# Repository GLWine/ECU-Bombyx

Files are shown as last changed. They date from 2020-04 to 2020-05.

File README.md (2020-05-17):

# ECU documentation for Bombyx mori





Thesis project on the effects of climate and gases in companies that produce silk. Use of an Arduino system called ECU-Bombyx (Environmental control unit - Bombyx Mori).

Purpose: to measure changes in temperature, humidity, eCO2 and total volatile organic compounds (TVOC) to correlate any effects on the yarn obtained.
The project consists of an Arduino, a humidity and temperature sensor, a clock module, an SD card shield and an SGP30 sensor for air quality.
Every 15 minutes The ECU-BM performs a reading that it saves in the SD.

<table cellspacing=”0″ cellpadding=”0″ width=”560″ border="0">
<tbody>
<tr>
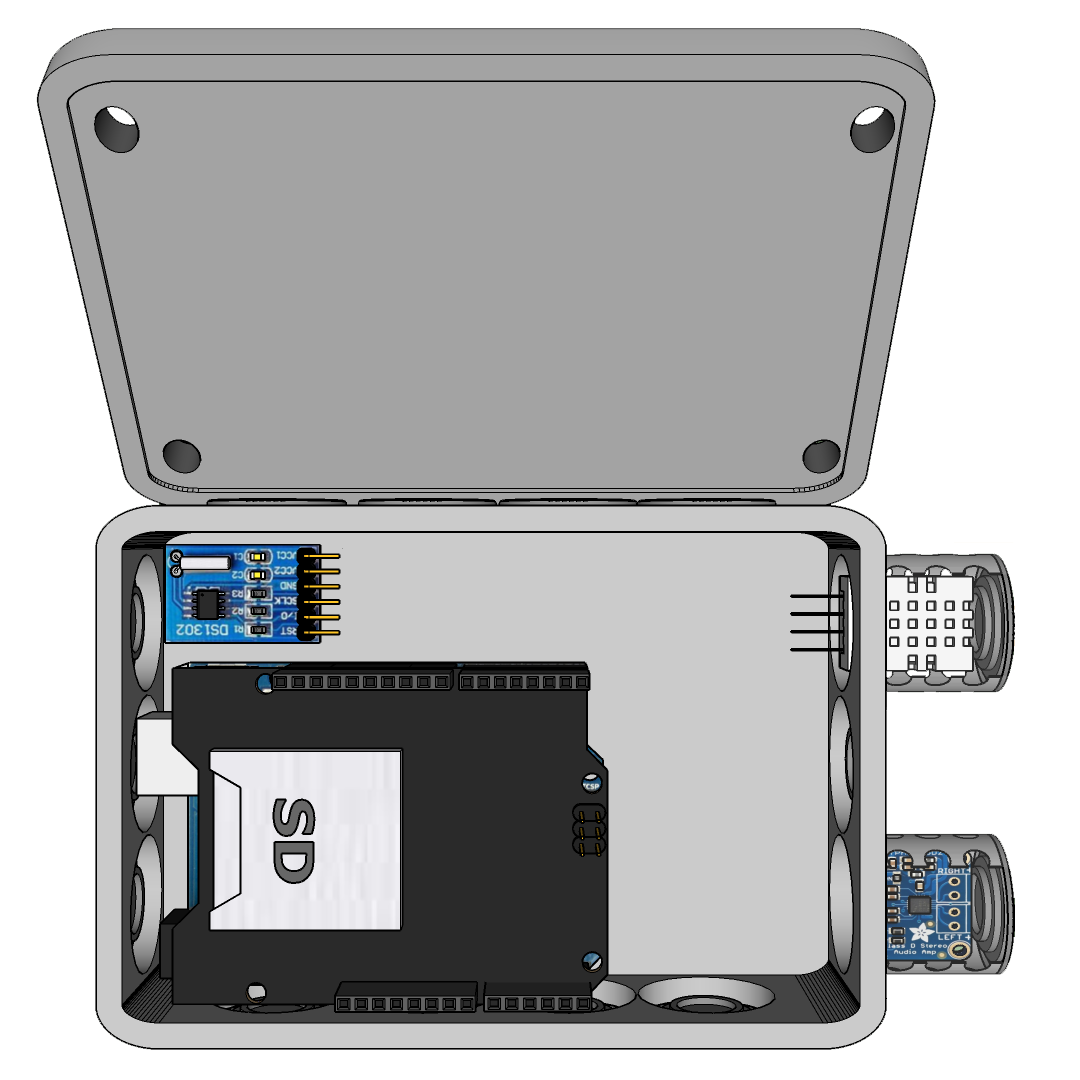
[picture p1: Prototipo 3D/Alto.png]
<td valign=”top” width=”250”></td>
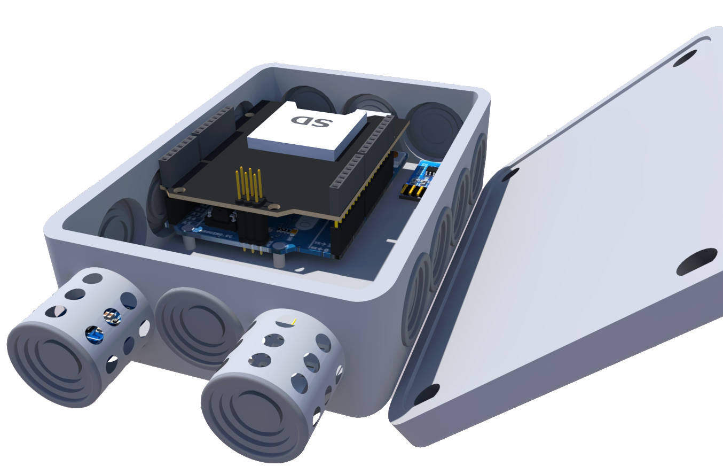
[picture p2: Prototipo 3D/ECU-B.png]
<td valign=”top” width=”250”></td>
</tr></tbody></table>

# Installation guide

## Phase 1: *wiring*
Before installing and starting make sure of the presence of these modules:
- DHT 22 sensor (temperature and humidity);
- Micro-SD module;
- RTC DS1302 module (clock);
- SGP30 air quality sensor;
- Arduino module one turn. 3;
Strictly carry out the wiring as indicated in the ECU-Bombyx image.

## Phase 2: *software installation*
Step 0: install the necessary libraries.

Step 1: install the ECU-Bombyx-Setter file from the Arduino IDE. In the "Serial monitor" view, make sure all modules respond.

--- Skip if the previous one is successful ---

Step 2: carefully check the wiring and that the modules are actually working.

Step 3: install the ECU-Bombyx-Base-Line file from the Arduino IDE. This is to find the baseline for the SGP30 sensor. Based on the [manufacturer's information](https://github.com/adafruit/DHT-sensor-library/pull/138 "Baseline Set & Get"), I created the code. This passage is of fundamental importance. The procedure lasts 12, it must be done for each SGP30 you have.

Step 4: install the ECU-Bombyx-Main file from the Arduino IDE. In the "Serial monitor" view, make sure that all modules respond and complete operations.

Final notes:
1. will start reading every 15 minutes writing in the micro-SD. The save format is .cvs with the company name.
2. If the DHT 22 module does not mount a 4K7 Ohm resistor, it is essential to solder one between DAT and VDD.
3. (optional) Add a 100nF capacitor between VDD and GND for filtering the waves.
3. There is a voluntary error in the ECU-BOMBYX-Main code. The reason is to remind those who use the code to set the variable that gives the name the file with the readings.

# Libraries

I made some changes to it based on this libbrerie of DHT [Pull requests #138](https://github.com/adafruit/DHT-sensor-library/pull/138 "Fixed signed/unsigned and unused parameter warnings")

The library to be imported with the correction is in the zip, it is sufficient to decompress it in the folder ..\Documents\Arduino\libraries\.

## Libraries List

Here are the lepers used for the code:

- Adafruit SGP30 Air Quality Sensor Breakout
  - Adafruit SGP30 Sensor by Adafruit V.1.2.0
- DS1302: Trickle-Charge Timekeeping Chip
  - RTC by Makuna V.2.3.4
- DHT22 temperature-humidity sensor + extras
  - DHT sensor librery by Adafruit V.1.3.9 **_modified_**

I recommend installing all the dependencies that arduino IDE offers

# License   

This program is free software: you can redistribute it and/or modify
it under the terms of the GNU General Public License as published by
the Free Software Foundation, either version 3 of the License, or
(at your option) any later version.

This program is distributed in the hope that it will be useful,
but WITHOUT ANY WARRANTY; without even the implied warranty of
MERCHANTABILITY or FITNESS FOR A PARTICULAR PURPOSE.  See the
GNU General Public License for more details.

You should have received a copy of the GNU General Public License
along with this program.  If not, see <http://www.gnu.org/licenses/>.

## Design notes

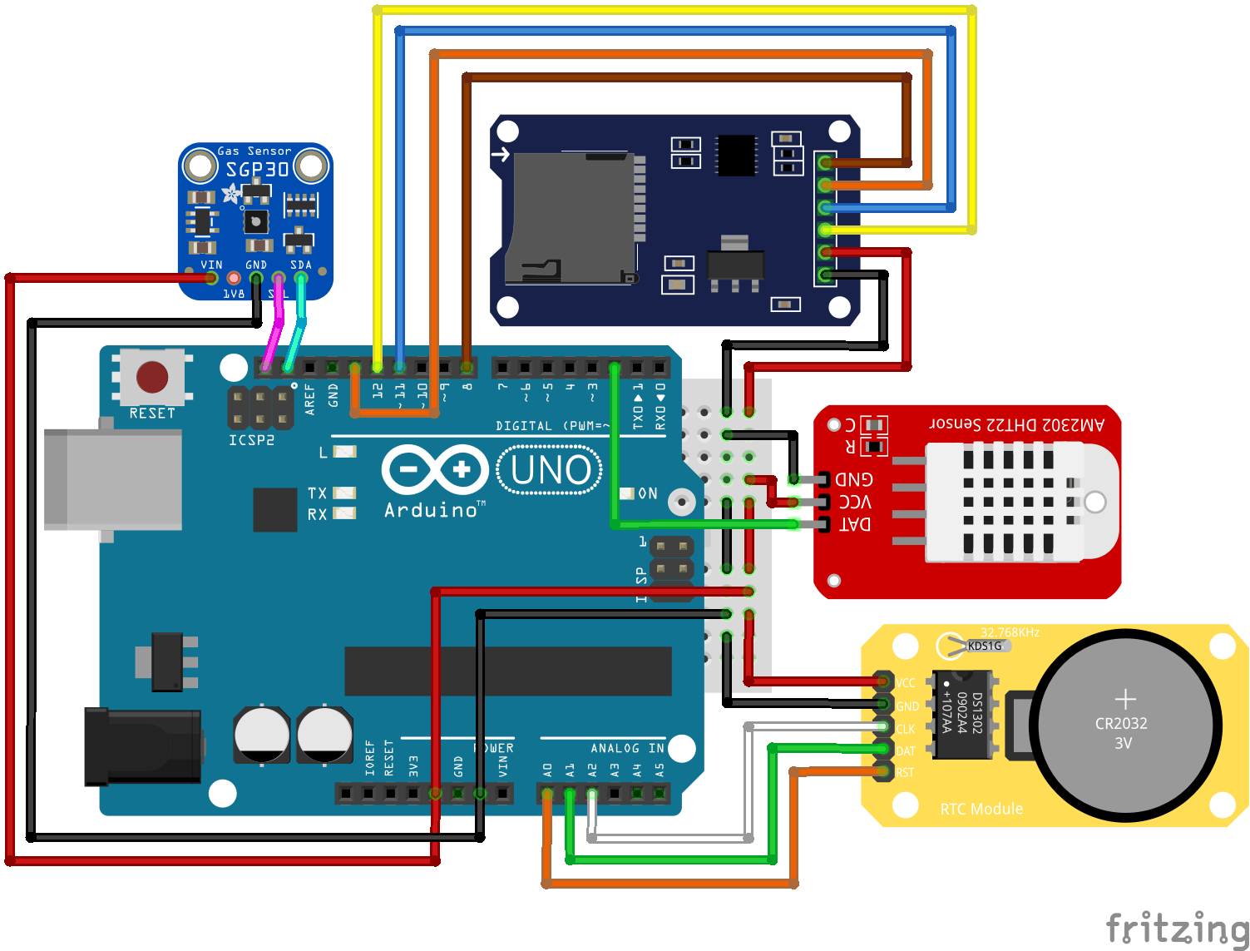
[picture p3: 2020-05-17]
ECU design on Fritzing/ECU-Bombyx.png

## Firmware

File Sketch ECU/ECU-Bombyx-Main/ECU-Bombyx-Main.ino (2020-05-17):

/* The following code is used to set the various components and to verify that 
 * everyone answers the call. It is written on the right serial monitor. 
 * The data are conveyed into a single variable then written into the SD.
 * 
 * modified 17 May 2020 by Giampiero Leserri
 */

// ADD the following Arduino libraries:
#include <SPI.h>            // standard Arduino library
#include <SD.h>             // standard Arduino library
#include <Wire.h>           // standard Arduino library
#include <Adafruit_SGP30.h> //Adafruit SGP30 Sensor by Adafruit V1.2.0
#include <ThreeWire.h>      // RTC: RTC by Makuna V.2.3.4
#include <RtcDS1302.h>      // RTC: RTC by Makuna V.2.3.4
#include <DHT.h>            /* DHT: DHT sensor librery by Adafruit V.1.3.9
                            *       Adafruit Unified Sensor by Adafruit V.1.1.2                        
                            *       Adafruit ADXL343 by Adafruit V.1.2.0 
                            */

// set up variables using the DHT 22:
#define DHTPIN 2          //Pin select DHT
#define DHTTYPE DHT22     // DHT 22  (AM2302), AM2321
DHT dht(DHTPIN, DHTTYPE); // Declare the DHT data pin and model to the DHT library

// set up variables using the SD utility library functions:
#define chipSelect 4 // declare the pin that is connected to the chip select
File myFile;         // the myFile object is created for the SD

// set up variables using the DS1302 RTC:
ThreeWire myWire(15, 16, 14); // DAT->pin A1, CLK->pin A2, RS->pin A0
RtcDS1302<ThreeWire> Rtc(myWire);
#define countof(a) (sizeof(a) / sizeof(a[0]))

// set up variables using the sgp30:
Adafruit_SGP30 sgp;
uint16_t TVOC_base, eCO2_base;
float temperature = 0; // [°C]
float humidity = 0;    // [%RH]
uint32_t getAbsoluteHumidity(float temperature, float humidity)
{
  // approximation formula from Sensirion SGP30 Driver Integration chapter 3.15
  const float absoluteHumidity = 216.7f * ((humidity / 100.0f) * 6.112f * exp((17.62f * temperature) / (243.12f + temperature)) / (273.15f + temperature)); // [g/m^3]
  const uint32_t absoluteHumidityScaled = static_cast<uint32_t>(1000.0f * absoluteHumidity);                                                                // [mg/m^3]
  return absoluteHumidityScaled;
}

// declaration of the Global variables make a string
//  for assembling the data to log
String dataOnTtheRow = "";

// Enter the initial company name without spaces followed by a progressive number
// for each ECU installed, also entering ".csv" (maximum 6.3 characters)
// Ex. Seta Etica ECU 1 => "SeEt01.csv"
const String company = "xxxxxx.csv"!;  // this error allows you not to forget to set the company name

// variable to which the 15 minutes to take the readings are added
uint32_t pouse = 0;
// Variable content in the if on line xxx,
// this causes every 4 readings to set the new baseline
int8_t c = 0;

//*********************************************************************************
void setup()
{
  // Open serial communications and wait for port to open:
  Serial.begin(9600); // 9600 bps serial port setting
  delay(500);

  rtcSet();
  sdSet();
  DHTSet();
  sgp30Set();
}

void loop()
{
  // If 15 minutes of use have passed a reading
  if (millis() > pouse)
  {
    // Further increase of 15 the pauseMain value, causes overflow
    pouse += (15UL * 60UL * 1000UL);
    heatingSgp30();

    delay(2000); // Safety delay in case of DHT reset
    rtcMain();
    DHTMain();
    sgp30Main();
    sdMain();
    c += 1;
  }
}
//---------------------------------------------------------------------------------

// Group of functions for setting the modules
//*********************************************************************************

// The function takes care of starting and if necessary
// setting the date and time of the DS1302
void rtcSet()
{
  Rtc.Begin();
  Serial.println(F("RTC initialized!"));

  if (Rtc.GetIsWriteProtected())
  {
    //      Serial.println(F("RTC was write protected, enabling writing now"));
    Rtc.SetIsWriteProtected(false);
  }

  if (!Rtc.GetIsRunning())
  {
    //      Serial.println(F("RTC was not actively running, starting now"));
    Rtc.SetIsRunning(true);
  }
}

// The function takes care of starting the SD module and, if necessary,
// creating a "CSV" file with the current date
void sdSet()
{
  Serial.print(F("Initializing SD card..."));

  // See if the card is present and can be initialized:
  if (!SD.begin(chipSelect))
  {
    Serial.println(F("Card failed, or not present"));
  }
  Serial.println(F("card initialized."));

  // Check if there is a file with the name given by the variable "company",
  // otherwise it creates and initializes it
  if (!SD.exists(company))
  {
    myFile = SD.open(company, FILE_WRITE);
    myFile.println(F("Data & Time;C-Temp;%-Humid;ppm-eCO2;ppb-TVOC;"));
    myFile.close();
    Serial.print(company);
    Serial.println(F(" file created"));
  }
}

// initialazied DHT22
void DHTSet()
{
  dht.begin();
  Serial.println(F("DHT22 initialized!"));
}

void sgp30Set()
{
  if (!sgp.begin())
  {
    Serial.println(F("Sensor not found :("));
  }
  else
  {
    Serial.println(F("SGP30 initialized!"));
  }
  Serial.print(F("Found SGP30 serial #"));
  Serial.print(sgp.serialnumber[0], HEX);
  Serial.print(sgp.serialnumber[1], HEX);
  Serial.println(sgp.serialnumber[2], HEX);

  // open the ECO2.TXT for reading:
  myFile = SD.open("eCO2.txt");
  if (myFile)
  {
    Serial.println(F("\neCO2.txt read... "));

    // read from the file until there's nothing else in it:
    while (myFile.available())
    {
      dataOnTtheRow = myFile.readStringUntil('\n');
      dataOnTtheRow.replace("\n", "");
      // goes to convert the string hexadecimal into a integer
      eCO2_base = strtoul(dataOnTtheRow.c_str(), NULL, 16);
      Serial.println(F("Print eCO2_base"));
      Serial.println(eCO2_base, HEX);
    }
    // close the file:
    myFile.close();
  }
  else
  {
    // if the file didn't open, print an error:
    Serial.println(F("error opening ECO2.TXT"));
  }

  // open the TVOC.TXT for reading:
  myFile = SD.open("TVOC.txt");
  if (myFile)
  {
    Serial.println(F("TVOC.TXT read... "));

    // read from the file until there's nothing else in it:
    while (myFile.available())
    {
      dataOnTtheRow = myFile.readStringUntil('\n');
      dataOnTtheRow.replace("\n", "");
      // goes to convert the string hexadecimal into a integer
      TVOC_base = strtoul(dataOnTtheRow.c_str(), NULL, 16);
      Serial.println(TVOC_base, HEX);
    }

    // close the file:
    myFile.close();
  }
  else
  {
    // if the file didn't open, print an error:
    Serial.println(F("error opening TVOC.TXT"));
  }

  // it sets the baseline calculated in 12 hours
  if (!sgp.setIAQBaseline(eCO2_base, TVOC_base))
  {
    Serial.println(F("the baseline was not written!"));
  }
}
//---------------------------------------------------------------------------------

// Group of functions for utilized the modules
//*********************************************************************************

// The function takes care of heating the sgp30 module
void heatingSgp30()
{
  humidity = dht.readHumidity();
  temperature = dht.readTemperature();
  sgp.setHumidity(getAbsoluteHumidity(temperature, humidity));
  for (int i = 0; i <= 30; i++)
  {
    sgp.IAQmeasure();
    delay(1000);
  }
  // Notice of end of heating
  Serial.println(F("heating finished"));

  if (c == 4)
  {
    sgp.getIAQBaseline(&eCO2_base, &TVOC_base);
    sgp.setIAQBaseline(eCO2_base, TVOC_base);
    c = 0;
  }
}

// The function starts writing in the string that forms the first line
void rtcMain()
{
  // I create a DateTime object and call it now
  // and pass it the constructor rtc.now();
  RtcDateTime now = Rtc.GetDateTime();
  printDateTime(now);

  if (!now.IsValid())
  {
    Serial.println();
    // Common Causes:
    // the battery on the device is low or even missing and
    // the power line was disconnected
    Serial.println(F("RTC lost confidence in the DateTime!"));
  }
}

// The function converts and writes the time to the dataOnTtheRow variable
void printDateTime(const RtcDateTime &dt)
{
  char datestring[20];

  snprintf_P(datestring,
             countof(datestring),
             PSTR("%04u/%02u/%02u %02u:%02u"),
             dt.Year(),
             dt.Month(),
             dt.Day(),
             dt.Hour(),
             dt.Minute());
  dataOnTtheRow = String(datestring);
  dataOnTtheRow += (F(";"));
}

// Function for reading humidity and temperature
void DHTMain()
{
  // Reading temperature or humidity takes about 250 milliseconds!
  // Sensor readings may also be up to 2 seconds 'old' (its a very slow sensor)
  float h = dht.readHumidity();
  // Read temperature as Celsius (the default)
  float t = dht.readTemperature();

  // Writing of the values read in the two variables
  if (isnan(h) || isnan(t))
  {
    Serial.println(F("Failed to read from DHT sensor!"));
  }

  // Passing data to the variable that will write to the SD
  dataOnTtheRow += (t);
  dataOnTtheRow += (F(";"));
  dataOnTtheRow += (h);
  dataOnTtheRow += (F(";"));
}

void sgp30Main()
{
  c = c + 1;
  delay(2000);
  // If you have a temperature / humidity sensor, you can set the absolute
  // humidity to enable the humditiy compensation for the air quality signals
  humidity = dht.readHumidity();
  temperature = dht.readTemperature();
  sgp.setHumidity(getAbsoluteHumidity(temperature, humidity));
  if (!sgp.IAQmeasure())
  {
    dataOnTtheRow += (F("sgp not read; sgp not read;"));
  }
  else
  {
    dataOnTtheRow += (sgp.eCO2);
    dataOnTtheRow += (F(";"));
    dataOnTtheRow += (sgp.TVOC);
    dataOnTtheRow += (F(";"));
  }
}

// Function that writes the data collected in the SD
void sdMain()
{
  // open the file. note that only one file can be open at a time,
  // so you have to close this one before opening another.
  myFile = SD.open(company, FILE_WRITE);

  // if the file is available, write to it:
  if (myFile)
  {
    myFile.println(dataOnTtheRow);
    myFile.close();
    Serial.println(F("String:"));
    Serial.println(dataOnTtheRow);
    Serial.print(company);
    Serial.println(F(" update!\n"));
  }
}
//---------------------------------------------------------------------------------
//Sketch uses 25922 bytes (80%) of program storage space. Maximum is 32256 bytes.
//Global variables use 1164 bytes (56%) of dynamic memory,
//leaving 884 bytes for local variables. Maximum is 2048 bytes.

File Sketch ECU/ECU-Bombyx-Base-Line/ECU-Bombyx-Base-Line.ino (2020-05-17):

/* The following code is used to set the starting baseline for the SGP30 module.
 * The calibration process lasts 12 hours, every 30 minutes from a partial response.
 * At the end he writes in the SD the two found values of the eCO2 and of the TVOC.
 * 
 * modified 17 May 2020 by Giampiero Leserri
 */

#include <SPI.h>
#include <SD.h>
#include <Wire.h>
#include <Adafruit_SGP30.h>
#include <DHT.h>

// set up variables using the DHT 22:
#define DHTPIN 2          //Pin select DHT
#define DHTTYPE DHT22     // DHT 22  (AM2302), AM2321
DHT dht(DHTPIN, DHTTYPE); // Declare the DHT data pin and model to the DHT library

// set up variables using the SGP30:
Adafruit_SGP30 sgp;
uint16_t TVOC_base, eCO2_base;
/* return absolute humidity [mg/m^3] with approximation formula
* @param temperature [°C]
* @param humidity [%RH]
*/
uint32_t getAbsoluteHumidity(float temperature, float humidity)
{
  // approximation formula from Sensirion SGP30 Driver Integration chapter 3.15
  const float absoluteHumidity = 216.7f * ((humidity / 100.0f) * 6.112f * exp((17.62f * temperature) / (243.12f + temperature)) / (273.15f + temperature)); // [g/m^3]
  const uint32_t absoluteHumidityScaled = static_cast<uint32_t>(1000.0f * absoluteHumidity);                                                                // [mg/m^3]
  return absoluteHumidityScaled;
}

// set up variables using the SD utility library functions:
#define chipSelect 4 // declare the pin that is connected to the chip select
// the myFile object is created for the SD
File myFilex;
File myFiley;

//
const unsigned long timeL = 44100000;  //12 hour
static unsigned long timeS1 = 60000;   // 1 minute
static unsigned long timeS2 = 1800000; //30 minute

//const unsigned long timeL = 600000; //10 minute
//static unsigned long timeS1 = 60000; // 1 minute
//static unsigned long timeS2 = 300000; //5 minute

void setup()
{
  Serial.begin(9600);

  Serial.print(F("Initializing SD card..."));

  if (!SD.begin(4))
  {
    Serial.println(F("initialization failed!"));
    while (1)
      ;
  }

  dht.begin();

  Serial.println(F("initialization done."));

  Serial.println(F("SGP30 test"));

  if (!sgp.begin())
  {
    Serial.println(F("Sensor not found :("));
    while (1)
      ;
  }
  Serial.print(F("Found SGP30 serial #"));
  Serial.print(sgp.serialnumber[0], HEX);
  Serial.print(sgp.serialnumber[1], HEX);
  Serial.println(sgp.serialnumber[2], HEX);
  Serial.println(F("Calibration start... (duration 12h)\n******************************"));

  // If you have a baseline measurement from before you can assign it to start, to 'self-calibrate'
  //sgp.setIAQBaseline(0x8E68, 0x8F41);  // Will vary for each sensor!
  myFilex = SD.open("Cali.csv", FILE_WRITE);

  // if the file is available, write to it:
  if (myFilex)
  {
    myFilex.println(F("eCO2;TVOC"));
    myFilex.close();
  }
  else
  {
    // if the file didn't open, print an error:
    Serial.println(F("error opening Cali.csv"));
  }
}
// creo una varibile per far andare l'if in basso alla riga 138
int i = 0;
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

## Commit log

2020-04-26 Added 3d rendering of the prototype
2020-05-04 Update ECU-Bombyx-Main.ino
    Change of the way to save files. This celt was born since the code tends to set the date at each start. If the RTC battery accidentally comes off, strange problems may arise. Now the file is created 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
    Bug fixing and code comments
2020-05-04 Info adding
    insertion of some explanations of the thesis project
2020-05-06 RTC DS1302 implementation
    implementation of the RTC DS1302 code to replace the RTC DS3231 model
    [ECU-Bombyx.fzz]
2020-05-06 Updated fritzy model
    Updated the wiring
    [ECU-Bombyx.fzz]
2020-05-06 Updated fritzy model 2
    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
    [ECU-Bombyx.fzz]
2020-05-07 Calibration code of the SGP30
    The code processes the data for 12 hours and at the end writes the calibration values to the serial and SD
2020-05-07 Calibration code of the SGP30
    The code processes the data for 12 hours and at the end writes the calibration values on serial and SD, creates 3 files 2 of the final reading and one of various readings at 30 minutes.
2020-05-17 DS1302 and SGP3231 added
    Replacing the DS3231 with the DS1302.
    Integration of the sesnosre SGP30 air quality, System which improves the calculations using humidity and temperature data.
2020-05-17 Code for the baseline of the SGP30 sensor
    Created a new code that takes care of calculating the Baseline, it takes 12 hours to obtain an efficient one.
